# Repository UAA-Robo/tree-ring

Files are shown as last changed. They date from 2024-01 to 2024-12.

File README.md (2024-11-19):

# Tree Ring Imaging Machine (TRIM)

Documentation can be viewed at [uaa-robo.github.io/tree-ring](https://uaa-robo.github.io/tree-ring/) and in the docs folder.

This code controls the Amscope camera (our model is the MU500 and MU1000).

The following files are taken from the SDK provided by AmScope [here](https://amscope.com/pages/software-downloads) when you select your camera and model:
* amcam.py - this file provides an API for the camera. For more information about the API, see [API.pdf](API.pdf).
* simplest.py - this file provides a simple example that opens the camera and grabs frames from the camera, though it does not display these frames.
* qt.py - this file provides an example that grabs frames from the camera and renders them in a GUI.
* libamacam.dylib - needed for mac
* win/ - contains drivers and dlls needed for windows

We created the following files:
* camera.py - Interfaces with images from the amcam or the webcam if no amcam is present.
* gui.py - Displays a gui that the user can use to run the automation script. Displays camera feed.
* automationScript.py -  Script that rotates the motor to shift the platform and trigger the camera to take pctures.

## Setup & Running
For setup, run `python -m pip install -r requirements.txt` to install the python requirements needed.

To execute this program run `python gui.py` in this directory.

## Bundle program into an executable for Windows
To compile this program, double-click on the `build.bat` script. An executable will be generated
in the dist folder.

Note: When building the program in "windowed" mode or "noconsole", Windows thinks its a virus. Building
it with the console window attached when running prevents that from happening.

<!-- Old instructions -->
<!-- To compile this program go open the terminal in the directory of gui.py and run `python -m PyInstaller gui.py --onefile --windowed`. This will not work on Mac due to strict camera permission.

When building the program into a binary, Windows will throw a 'severe' threat warning. This is
because the software lacks an official Microsoft signature. To bypass this, open Windows Security,
click on 'Virus & threat protection,' and click on the link 'Manage settings' under 'Virus & threat
protection settings.' At the bottom of this menu there is a link to 'Add or remove exclusions.'
Add an exclusion of the type 'Folder,' and select the directory containing the program. Now running
the above command will successfully build the executable. -->

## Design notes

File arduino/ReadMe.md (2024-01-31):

To run the arduino code make sure to set the board type to arduino nano in the arduino IDE

Arguments that can be passed to Arduino
Z = Zero Platform
H = Make Motor Turn Clockwise
L = Make Motor Turn CounterClockwise
R = Move Motor 1 Increment
+ = Increase Motor Turn Length by 1/10
- = Decrease Motor Turn Length by 1/10
= = Get Motor Turn Length

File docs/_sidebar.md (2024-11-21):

* [Instructions](instructions.md)
* [How to Build](how_to_build/construction_instructions.md)
    * [Bill of Materials](how_to_build/BOM.md)
* [Upgrades](upgrades.md)
* [Troubleshooting](troubleshooting/troubleshooting.md)
    * [Motor Not Moving](troubleshooting/motor_movement.md)
    * [Motor is Loud](troubleshooting/motor_noises.md)
    * [No Arduino Connected](troubleshooting/no_arduino.md)
    * [No Camera Detected](troubleshooting/no_camera.md)
    * [Optimal Camera Settings](troubleshooting/optimal_settings.md)
* [Code Overview](code.md)
* [Contributing](contributing.md)

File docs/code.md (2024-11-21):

# Code Explanations
Refer to the comments in our code in our github for more in-depth explanations of each function. Below iss an overview.

## GUI 
* gui.py
The GUI class contains all the logic for displaying the user interface. It has a callback to Camera to display the camera video stream to the user. The GUI will display any warnings or errors that show up as popups.The user can enter the following information:
* **Image/Core name**: This is used to name the images when saving, with a prepended image number. For example if `core_alpha` is entered, the images would be named `core_alpha_1.jpg`, `core_alpha_2.jpg`, etc
* **Core Length (cm)**: This is the length of the core in cm.
* **Shift Length (mm)**: This is the length to shift the core sample after taking a picture.

Then the user can start the automation program in the Automation class. We suggest setting the image path to the desired location where you want TRIM to put the folder of images it creates, otherwise it will default to the desktop. After selection, the automation immediately starts. The user can stop the program at any time by pressing the pause button, and can later resume the automation by pressing play.

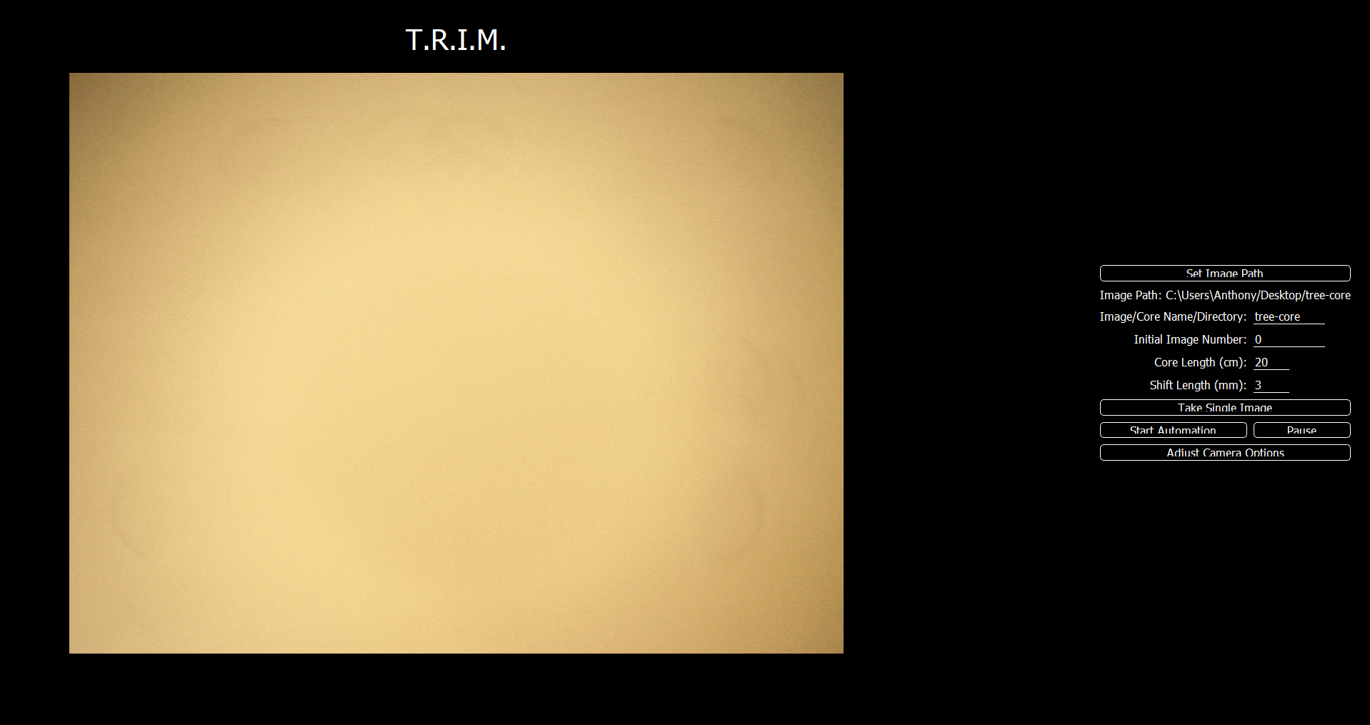
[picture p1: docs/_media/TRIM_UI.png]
GUI


### Camera Options

Pressing the **Adjust Camera Options** button will open a new window that allows the user to adjust camera video and save options. Pressing **Save** will save them to a file called `camera_configuration.yaml` in the directory where the program is located. By default, the program loads the settings from this file on startup. Pressing **Reset** will reset any changes back to this file, or if it is missing, the optimal settings. If you need the actual default settings in the API or a copy of the optimal settings file, go to [this link](troubleshooting/optimal_settings.md) to get the original file.

## Automation 
* automationScript.py

The Automation class contains all the code for automating the tree ring process. It references the Camera class (in camera.py) to save images and the Arduino class (in the same file) to send signals to the arduino to connect and rotate the motor. The primary method of this class is start_automation. It calculates the number of times to move the tree ring based on the length input. Then it moves the platform that many times by that length, taking and saving a picture before each shift. 

The Arduino Class is a wrapper for the commands sent to the Arduino. The Arduino defaults to a shift length of 3mm and the following commands are Currently the following high level methods are implemented:
* `connect_to_arduino` - Attempts to connect to the arduino.
* `update_shift_length` - Updates the shift length that the arduino spins the motor (defaults to 3mm).
* `shift_right` - Spins the motor left to shift the platform RIGHT by the shift length.

## Camera 
* camera.py
* amcam.py (Amcam API)
* amcam.dll, libamcam.dylib (compiled C code used by amcam.py)
* /win (windows drivers)

The Camera class holds all properties for the camera and wraps all interactions with it. When the program begins and initializes the Camera, a callback method is loaded into the Amcam API. The Amcam API controls the camera, and by manipulating the contents of this callback method, we can choose to act on the events being sent from the camera (in this case we use `AMCAM_EVENT_IMAGE` and `AMCAM_EVENT_STILLIMAGE). The microscope image quality is left as default in all settings but the saturation, which is adjusted to around 37.6% of its range (96 / 255).

### Using the Microscope Camera
The Amcam camera starts its own thread, seen by `StartPullModeWithCallback()` in `connect_stream`, and runs the callback method first loaded in the init method. From then on, the camera runs asynchronously to the main thread, calling the static method, `camera_callback`. This callback pulls the camera's image into a byte array, converts it to a QImage, and saves it in the class for extraction by the program later. When an image is taken, the camera pauses the preview to take a still image (a full-resolution picture). The callback waits for a signal from the camera that it is done before saving the image to the specified directory.

### No Microscope Camera
If the microscope camera could not be loaded in the first place, the **cv2** library is used to load the next available camera (called `WEBCAM` in the camera type). In this case the Amcam API is not running its own thread, so instead of using the callback method, `connect_stream` starts a new thread for streaming from this camera, paralleling the Amcam API's behavior.

## Arduino 
* arduino/tree-ring/tree-ring.ino

The tree-ring.ino file holds the entirety of the code on the arduino. When powered on the arduino first runs the `setup()` function and once that is complete it will immediately start the `loop()` function. From there the arduino waits for a signal from the computer to start doing any actions.

Arguments that can be passed to Arduino  
`H`  Make Motor Turn Clockwise  
`L`  Make Motor Turn CounterClockwise  
`R`  Move Motor 1 Increment  
`+`  Increase Motor Turn Length by 1/10  
`-`  Decrease Motor Turn Length by 1/10  
`=`  Get Motor Turn Length

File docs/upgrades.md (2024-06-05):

# Upgrade Instructions
This guide provides easy-to-follow instructions on upgrading components of the TRIM software
solution.

## Camera
TRIM was originally designed for AmScope cameras, and so it utilizes the AmScope SDK. This means that AmScope cameras are preferred. As a backup, TRIM also supports cameras covered by the OpenCV library, but the advanced features are not supported for these cameras and they will take images at their default resolutions. It recommended to stay within the AmScope family, __.

The SDK used is specific to the camera, however. This means that it is necessary to install a new SDK on a new camera upgrade. These are the steps to upgrade the camera:

1. The new camera comes with a USB flash drive containing drivers. It also contains an up-to-date SDK that supports the new camera.
    - Plug the flash drive in and open the folder. First install the drivers. This can be done by either executing the `AmScopeMicroDshowSetup.exe` in the SDK folder, or installing the drivers manually (located in SDK/amcamsdk.20231217.zip/win/drivers/). The former method also installs the official AmScope software.
2. After installing the drivers, open a new window to the tree-ring source code folder.
3. Remove (keep somewhere else in case) the following files: `amcam.py`, `amcam.dll`, and `libamcam.dylib`.
4. Open up SDK/amcamsdk.20231217.zip and unzip it. Inside this directory, copy the following files into the root folder of the tree-ring source code folder:
    - `python/amcam.py`
    - `win/x64/amcam.dll`
    - `mac/x64+arm64/libamcam.dylib`

That should be it! The camera should be detected by the software now.

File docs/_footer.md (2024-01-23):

<b><br>
____
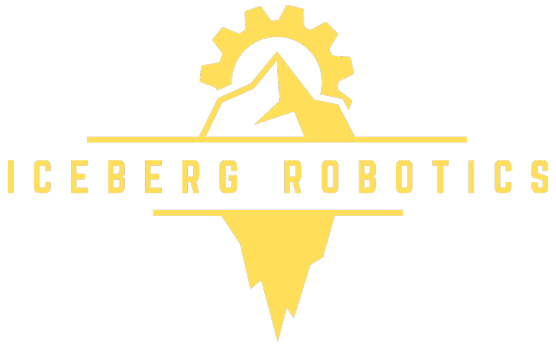
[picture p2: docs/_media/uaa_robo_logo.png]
:size=8%
 
<!-- ***Documentation maintained by [UAA Iceberg Robotics](http://uaarobotics.com).*** -->

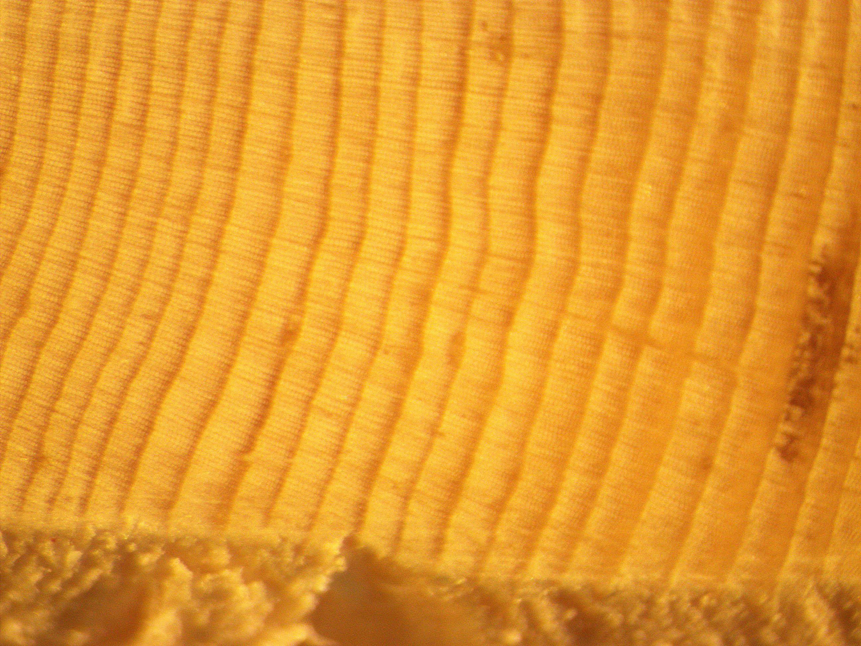
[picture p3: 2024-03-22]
Tree_Core_000.jpg

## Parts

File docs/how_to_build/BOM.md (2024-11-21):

# Bill of Materials

If this is not filled out by 11/22/2024 please create an issue on the Github repository.

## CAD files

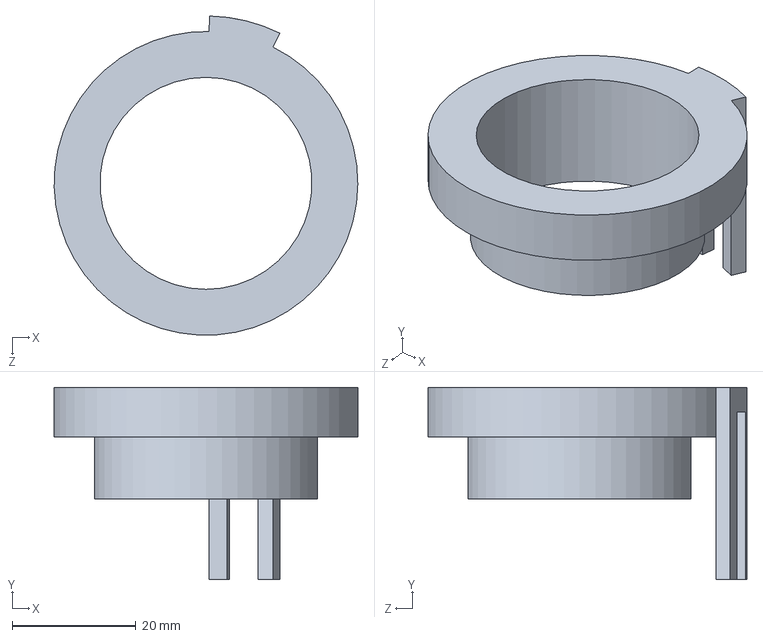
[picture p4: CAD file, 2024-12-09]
cad_models/TRIM MU500 Adapter.SLDPRT
49.0 x 31.0 x 51.5 mm

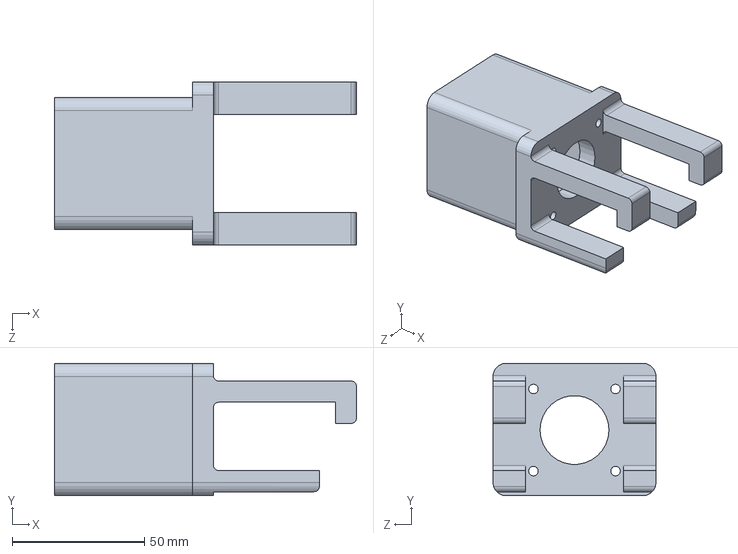
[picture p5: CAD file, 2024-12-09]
cad_models/TRIM Motor Mount.SLDPRT
114.0 x 50.0 x 61.5 mm

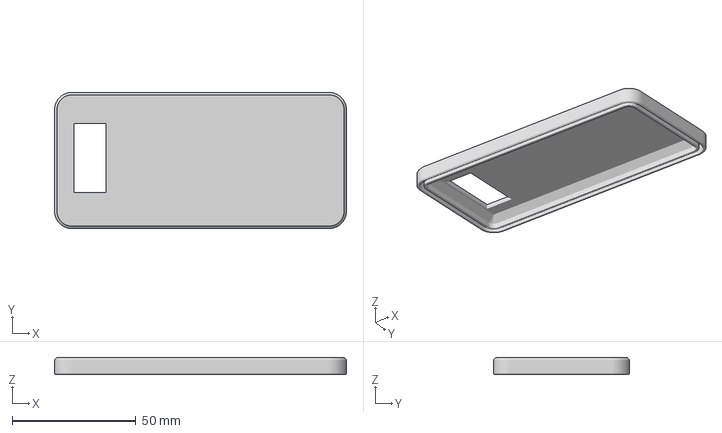
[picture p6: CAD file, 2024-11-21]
cad_models/TRIM Lid.3mf
118.2 x 55.1 x 7.00 mm

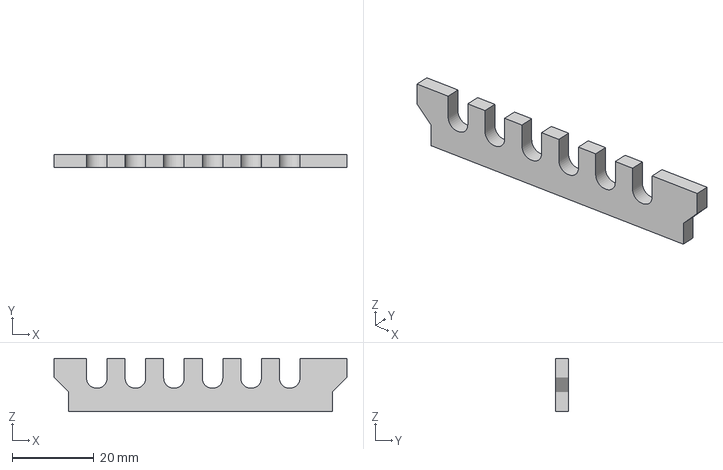
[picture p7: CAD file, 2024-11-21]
cad_models/TRIM Board Lock.3mf
71.5 x 3.20 x 13.0 mm

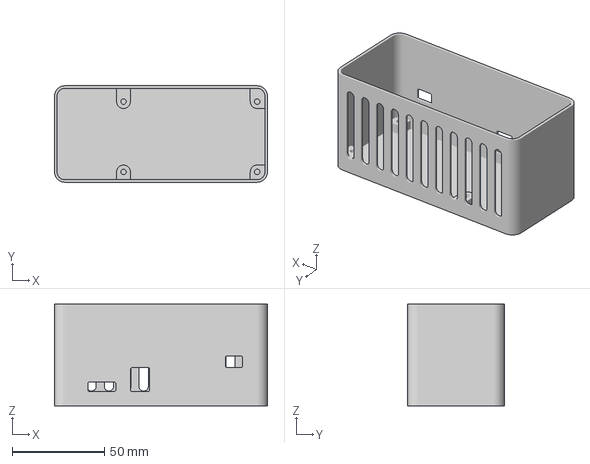
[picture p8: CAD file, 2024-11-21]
cad_models/TRIM Enclosure.3mf
115.4 x 52.3 x 55.0 mm

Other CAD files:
cad_models/TRIM MU500 Adapter.STL
cad_models/TRIM Motor Mount.STL

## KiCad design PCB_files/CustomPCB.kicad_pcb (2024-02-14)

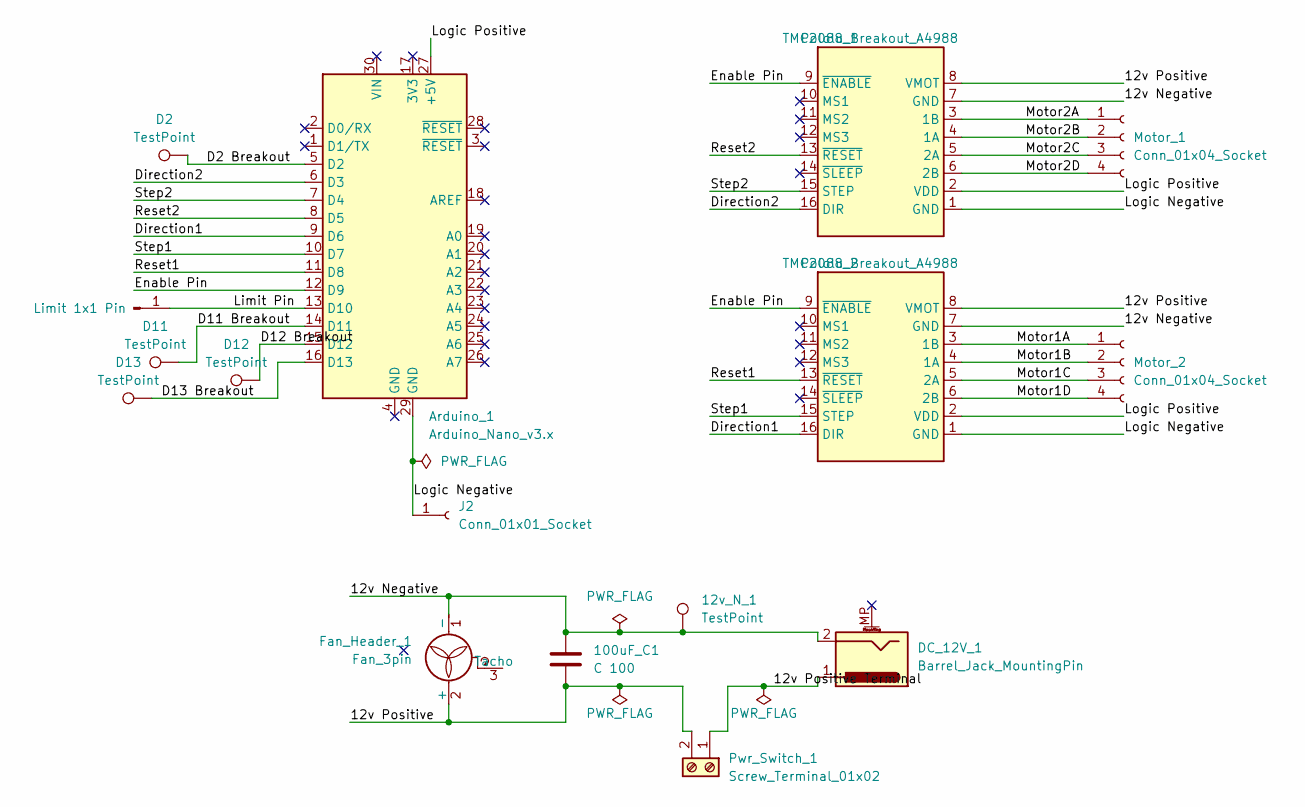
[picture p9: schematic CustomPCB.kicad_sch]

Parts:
12v_N_1: TestPoint; TestPoint_Pad_1.5x1.5mm
100uF_C1: C 100; CP_Radial_D8.0mm_P5.00mm
Arduino_1: Arduino_Nano_v3.x; Arduino_Nano
D2, D11, D12, D13: TestPoint; TestPoint_Pad_1.5x1.5mm
DC_12V_1: Barrel_Jack_MountingPin; BarrelJack_Horizontal
Fan_Header_1: Fan_3pin; FanPinHeader_1x03_P2.54mm_Vertical
J1: Limit 1x1 Pin; PinHeader_1x01_P2.54mm_Vertical
J2: Conn_01x01_Socket; PinHeader_1x01_P2.54mm_Vertical
Motor_1, Motor_2: Conn_01x04_Socket; PinSocket_1x04_P2.54mm_Vertical
Pwr_Switch_1: Screw_Terminal_01x02; TerminalBlock_bornier-2_P5.08mm
TMC2088_1, TMC2088_2: Pololu_Breakout_A4988; Pololu_Breakout-16_15.2x20.3mm

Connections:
/12v Negative: 12v_N_1.1, 100uF_C1.2, DC_12V_1.2, Fan_Header_1.1 (-), TMC2088_1.7 (GND), TMC2088_2.7 (GND)
/12v Positive: 100uF_C1.1, Fan_Header_1.2 (+), Pwr_Switch_1.2, TMC2088_1.8 (VMOT), TMC2088_2.8 (VMOT)
/12v Positive Terminal: DC_12V_1.1, Pwr_Switch_1.1
/D2 Breakout: Arduino_1.5 (D2), D2.1
/D11 Breakout: Arduino_1.14 (D11), D11.1
/D12 Breakout: Arduino_1.15 (D12), D12.1
/D13 Breakout: Arduino_1.16 (D13), D13.1
/Direction1: Arduino_1.9 (D6), TMC2088_2.16 (DIR)
/Direction2: Arduino_1.6 (D3), TMC2088_1.16 (DIR)
/Enable Pin: Arduino_1.12 (D9), TMC2088_1.9 (~ENABLE), TMC2088_2.9 (~ENABLE)
/Limit Pin: Arduino_1.13 (D10), J1.1
/Logic Negative: Arduino_1.29 (GND), J2.1, TMC2088_1.1 (GND), TMC2088_2.1 (GND)
/Logic Positive: Arduino_1.27 (+5V), TMC2088_1.2 (VDD), TMC2088_2.2 (VDD)
/Motor1A: Motor_2.1, TMC2088_2.3 (1B)
/Motor1B: Motor_2.2, TMC2088_2.4 (1A)
/Motor1C: Motor_2.3, TMC2088_2.5 (2A)
/Motor1D: Motor_2.4, TMC2088_2.6 (2B)
/Motor2A: Motor_1.1, TMC2088_1.3 (1B)
/Motor2B: Motor_1.2, TMC2088_1.4 (1A)
/Motor2C: Motor_1.3, TMC2088_1.5 (2A)
/Motor2D: Motor_1.4, TMC2088_1.6 (2B)
/Reset1: Arduino_1.11 (D8), TMC2088_2.13 (~RESET)
/Reset2: Arduino_1.8 (D5), TMC2088_1.13 (~RESET)
/Step1: Arduino_1.10 (D7), TMC2088_2.15 (STEP)
/Step2: Arduino_1.7 (D4), TMC2088_1.15 (STEP)

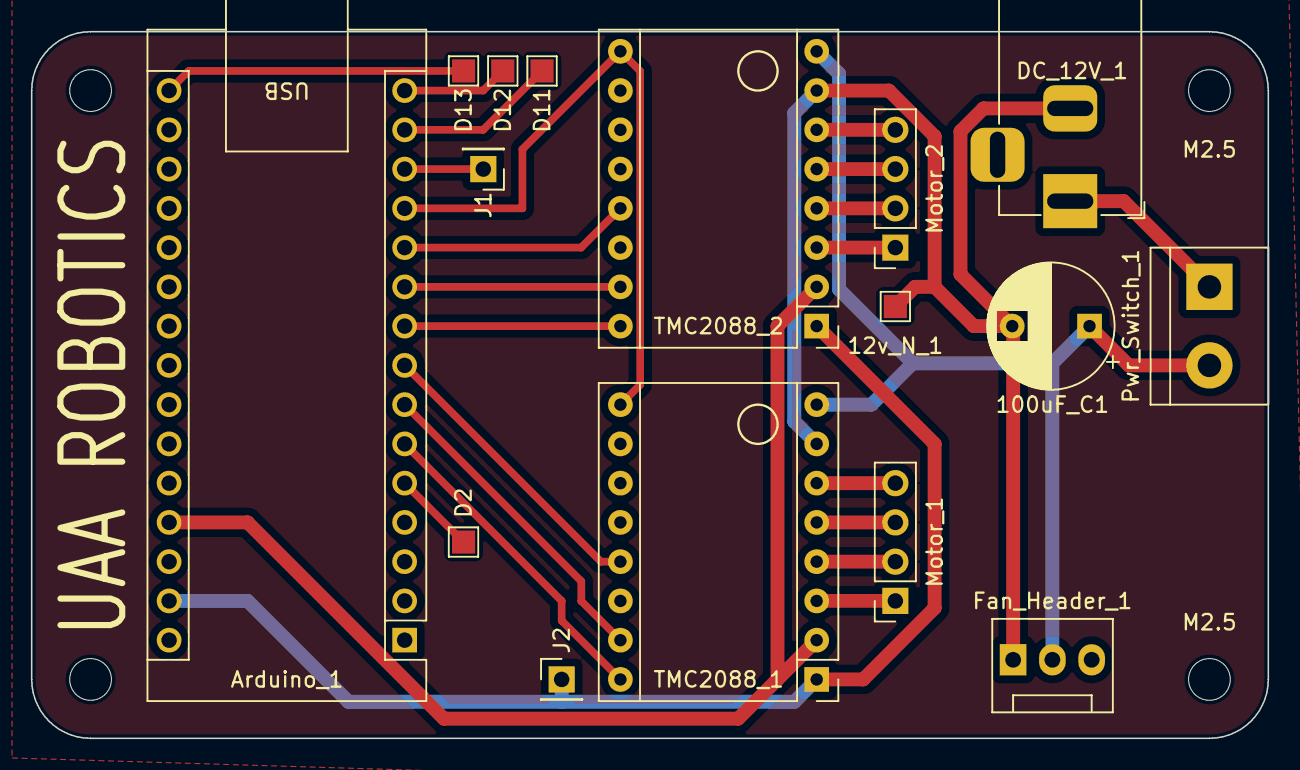
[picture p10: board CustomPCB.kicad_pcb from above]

Board: 2 copper layers, 80.0 x 45.7 mm, 20 parts (0 on the bottom side), 25 nets.

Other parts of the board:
M2.5, M2.5#2, M2.5#3, M2.5#4: MountingHole_2.7mm_M2.5

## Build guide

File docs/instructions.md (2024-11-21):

# Instructions for Use

1. Open the Application.

     

2. Setup your tree ring sample on the tray, so it is at the left edge of the microscope camera. Make sure too focus the camera properly.

3. Set the path where you would like TRIM to put the images.

4. Input your sample length (default is 20cm), and the amount you would like shift the sample each time (default is 3mm).

5. Select "Start Automation".

6. Let the script run. When it finishes it will say "Automation Stopped".

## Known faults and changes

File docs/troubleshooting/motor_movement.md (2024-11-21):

# Motor is not Moving

If the motor is not moving, please ensure that the switch ontop of TRIM's box is flipped to the ON position and that it is plugged in. If it is still not moving, please unseat and reseat all motor wires and ensure the motor drivers are pressed firmly in place.

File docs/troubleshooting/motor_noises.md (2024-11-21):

# Motor is Making Loud Noises

If the motor is loud please try changing the order of the motor's wires. This is often caused by the wires being in the wrong order.

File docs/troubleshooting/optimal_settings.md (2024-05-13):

# Optimal Settings for the Camera

The camera has a number of defaults for its image settings. However, through testing these have been found to be sub-optimal. The following table demonstrates the default and optimal settings for each camera setting.

| Camera Setting         | Range     | Default  | Optimal   |
| ---------------------- | --------- | -------- | --------- |
| Auto-Expo Enabled      | 1/0       |  1       |  0        |
| Auto Exposure Target   |   16~235  |  120     |  120      |
| Temperature            | 2000~15000|  6503    |  11616    |
| Tint                   | 200~2500  |  1000    |  925      |
| Level Range            | 0~255 x 4 | L(0,0,0,0) H(255,255,255,255)    | L(0,0,0,0) H(255,255,255,255)   |
| Contrast               | -100~100  |  0       |  0        |
| Hue                    | -180~180  |  0       |  0        |
| Saturation             | 0~255     |  128     |  126      |
| Brightness             | -64~64    |  0       |  -64      |
| Gamma                  | 20~180    |  100     |  100      |
| WBGain                 | -127~127 x 3   |  (0,0,0)       |  (0,0,0)       |
| Sharpening             | 0~500     |  0       |  500      |
| Linear Tone Mapping    | 1/0       |  1       |  0        |
| Curved Tone Mapping    | 2/1/0     |  2 (Logarithmic)     |  1 (Polynomial)      |

To configure the camera to the optimal settings, copy the following text block into a file called
`camera_configuration.yaml` in the directory where the program's exe is in.

**For a Leica KL 1500LCD light:**
```yaml
auto_expo: 0
brightness: 16
contrast: 0
curve: Polynomial
exposure: 50
fformat: tiff
gamma: 100
hue: 0
levelrange_high:
- 255
- 255
- 255
- 255
levelrange_low:
- 0
- 0
- 0
- 0
linear: 0
saturation: 96
sharpening: 500
temp: 6503
tint: 1000
wbgain:
- 0
- 0
- 0

```

**For a ring light:**
```yaml
auto_expo: 0
brightness: -64
contrast: 0
curve: Polynomial
exposure: 120
fformat: tiff
gamma: 100
hue: 0
levelrange_high:
- 255
- 255
- 255
- 255
levelrange_low:
- 0
- 0
- 0
- 0
linear: 0
saturation: 126
sharpening: 500
temp: 11616
tint: 925
wbgain:
- 0
- 0
- 0

```

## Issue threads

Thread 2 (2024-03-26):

### ISSUE TITLE
Capturing exposure events

### ISSUE THREAD

**Issue by richbai90** [UAA-Robo/tree-ring#2]
Hello,

I am writing because you are the only repo on Github I could find that was actively maintaining a project that utilizes the Amscope API. I'm using the AMCAM_EVENT_EXPO_START and AMCAM_EVENT_EXPO_END events, respectively, but they are not triggered when using pull mode, at least not when the camera is in video mode. Have you tried to use these events or other events besides AMCAM_EVENT_IMAGE in your work?

**Comment by Dawson-Packer** [comment]
Our project has only used AMCAM_EVENT_IMAGE so far so I’m sorry to say we can’t help you. If we learn anything new, we’ll make sure to send it your way.

**Comment by richbai90** [comment]
It's not supported with our camera. Closing, but thank you for replying.

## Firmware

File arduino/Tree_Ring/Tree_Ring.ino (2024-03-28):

int DIRECTION_PIN = 3;
int STEPPER_PIN = 4;
int LIMIT_SWITCH_PIN = 10;
int ENABLE_PIN = 9;
int RESET_PIN = 5;

int incoming_byte;

bool IS_CLOCKWISE = true;
bool IS_ACTIVE = false;

int active_counter = 0;
int rotate_amount = 161;//1600; //steps per revolution for 200 pulses = 360 degree full cycle rotation
int millimeters = 30;
int original_millimeters = millimeters;
int actual_movement = rotate_amount * millimeters;

void setup()
{
  /* 
	@brief   Setup the arduino upon power on.
  */
  pinMode(ENABLE_PIN, OUTPUT);
  pinMode(DIRECTION_PIN, OUTPUT);
  pinMode(STEPPER_PIN, OUTPUT);
  pinMode(LIMIT_SWITCH_PIN, INPUT_PULLUP);
  digitalWrite(DIRECTION_PIN, LOW);
  digitalWrite(STEPPER_PIN, LOW);
  activate();
  Serial.begin(9600);
}


void step(boolean dir,int steps)
 {
  /*
	@brief   This makes the motor move by a set amount. 
  @param dir   Direction the Motor Moves.
  @param stepts   Steps for the motor to turn. Minimum number of steps is 600, add more to go slower.
  */

 digitalWrite(DIRECTION_PIN,dir);

 for(int i=0;i<steps;i++)
 {
   digitalWrite(STEPPER_PIN, HIGH);
   delayMicroseconds(150);//Adjust the speed of motor. Increase the value, motor speed become slower.
   digitalWrite(STEPPER_PIN, LOW);
   delayMicroseconds(150);
 }
}

void activate(){
  /* 
	@brief   Wake up the motor driver.
  */
  if(!IS_ACTIVE){
    active_counter = 0;
    digitalWrite(ENABLE_PIN, LOW);
    digitalWrite(RESET_PIN, LOW);
    IS_ACTIVE = true;
    delayMicroseconds(1000);
  }
}


void deactivate(){
  /* 
	@brief   Put the motor driver to sleep. This saves power and makes the motor not heat up.
  */
  digitalWrite(ENABLE_PIN, HIGH);
  digitalWrite(RESET_PIN, HIGH);
  IS_ACTIVE = false;
}


void loop()
{
  /* 
	@brief   Update loop.
  */
  if(Serial.available()) {
    incoming_byte = Serial.read();
    if(incoming_byte == 72) { // H Set platform to rotate clockwise.
      Serial.write("Clockwise");
      IS_CLOCKWISE = true;
    } 
    if(incoming_byte == 76) { // L Set platform to rotate anticlockwise.
      Serial.write("AntiClockwise");
      IS_CLOCKWISE = false;
    }
    if(incoming_byte == 77) { // M Move the platform.
      activate();
      step(IS_CLOCKWISE, actual_movement);
    }
    if(incoming_byte == 82) { // R Reset Rotation Amount.
      millimeters = original_millimeters;
      Serial.write(millimeters);
    }
    if(incoming_byte == 43) { // + Increase Rotation Amount.
      millimeters = millimeters + 1;
      Serial.write(millimeters);
    }
    if(incoming_byte == 45) { // - Decrease Rotation amount.
      millimeters = millimeters - 1;
      Serial.write(millimeters);
    }
    if(incoming_byte == 61) { // = Get current Rotation Amount.
      Serial.write(millimeters);
    }
    actual_movement = rotate_amount * millimeters;
  }

  // Put motor to sleep if not in use.
  active_counter++;
  if(active_counter == 6000) {
    deactivate();
  }
}

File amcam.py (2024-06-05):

"""Version: 55.24172.20231217
We use ctypes to call into the amcam.dll/libamcam.so/libamcam.dylib API,
the python class Amcam is a thin wrapper class to the native api of amcam.dll/libamcam.so/libamcam.dylib.
So the manual en.html(English) and hans.html(Simplified Chinese) are also applicable for programming with amcam.py.
See them in the 'doc' directory:
   (1) en.html, English
   (2) hans.html, Simplified Chinese
"""
import sys, ctypes, os.path

AMCAM_MAX = 128

AMCAM_FLAG_CMOS                = 0x00000001          # cmos sensor
AMCAM_FLAG_CCD_PROGRESSIVE     = 0x00000002          # progressive ccd sensor
AMCAM_FLAG_CCD_INTERLACED      = 0x00000004          # interlaced ccd sensor
AMCAM_FLAG_ROI_HARDWARE        = 0x00000008          # support hardware ROI
AMCAM_FLAG_MONO                = 0x00000010          # monochromatic
AMCAM_FLAG_BINSKIP_SUPPORTED   = 0x00000020          # support bin/skip mode
AMCAM_FLAG_USB30               = 0x00000040          # usb3.0
AMCAM_FLAG_TEC                 = 0x00000080          # Thermoelectric Cooler
AMCAM_FLAG_USB30_OVER_USB20    = 0x00000100          # usb3.0 camera connected to usb2.0 port
AMCAM_FLAG_ST4                 = 0x00000200          # ST4
AMCAM_FLAG_GETTEMPERATURE      = 0x00000400          # support to get the temperature of the sensor
AMCAM_FLAG_HIGH_FULLWELL       = 0x00000800          # high fullwell capacity
AMCAM_FLAG_RAW10               = 0x00001000          # pixel format, RAW 10bits
AMCAM_FLAG_RAW12               = 0x00002000          # pixel format, RAW 12bits
AMCAM_FLAG_RAW14               = 0x00004000          # pixel format, RAW 14bits
AMCAM_FLAG_RAW16               = 0x00008000          # pixel format, RAW 16bits
AMCAM_FLAG_FAN                 = 0x00010000          # cooling fan
AMCAM_FLAG_TEC_ONOFF           = 0x00020000          # Thermoelectric Cooler can be turn on or off, support to set the target temperature of TEC
AMCAM_FLAG_ISP                 = 0x00040000          # ISP (Image Signal Processing) chip
AMCAM_FLAG_TRIGGER_SOFTWARE    = 0x00080000          # support software trigger
AMCAM_FLAG_TRIGGER_EXTERNAL    = 0x00100000          # support external trigger
AMCAM_FLAG_TRIGGER_SINGLE      = 0x00200000          # only support trigger single: one trigger, one image
AMCAM_FLAG_BLACKLEVEL          = 0x00400000          # support set and get the black level
AMCAM_FLAG_AUTO_FOCUS          = 0x00800000          # support auto focus
AMCAM_FLAG_BUFFER              = 0x01000000          # frame buffer
AMCAM_FLAG_DDR                 = 0x02000000          # use very large capacity DDR (Double Data Rate SDRAM) for frame buffer. The capacity is not less than one full frame
AMCAM_FLAG_CG                  = 0x04000000          # support Conversion Gain mode: HCG, LCG
AMCAM_FLAG_YUV411              = 0x08000000          # pixel format, yuv411
AMCAM_FLAG_VUYY                = 0x10000000          # pixel format, yuv422, VUYY
AMCAM_FLAG_YUV444              = 0x20000000          # pixel format, yuv444
AMCAM_FLAG_RGB888              = 0x40000000          # pixel format, RGB888
AMCAM_FLAG_RAW8                = 0x80000000          # pixel format, RAW 8 bits
AMCAM_FLAG_GMCY8               = 0x0000000100000000  # pixel format, GMCY, 8 bits
AMCAM_FLAG_GMCY12              = 0x0000000200000000  # pixel format, GMCY, 12 bits
AMCAM_FLAG_UYVY                = 0x0000000400000000  # pixel format, yuv422, UYVY
AMCAM_FLAG_CGHDR               = 0x0000000800000000  # Conversion Gain: HCG, LCG, HDR
AMCAM_FLAG_GLOBALSHUTTER       = 0x0000001000000000  # global shutter
AMCAM_FLAG_FOCUSMOTOR          = 0x0000002000000000  # support focus motor
AMCAM_FLAG_PRECISE_FRAMERATE   = 0x0000004000000000  # support precise framerate & bandwidth, see AMCAM_OPTION_PRECISE_FRAMERATE & AMCAM_OPTION_BANDWIDTH
AMCAM_FLAG_HEAT                = 0x0000008000000000  # support heat to prevent fogging up
AMCAM_FLAG_LOW_NOISE           = 0x0000010000000000  # support low noise mode (Higher signal noise ratio, lower frame rate)
AMCAM_FLAG_LEVELRANGE_HARDWARE = 0x0000020000000000  # hardware level range, put(get)_LevelRangeV2
AMCAM_FLAG_EVENT_HARDWARE      = 0x0000040000000000  # hardware event, such as exposure start & stop
AMCAM_FLAG_LIGHTSOURCE         = 0x0000080000000000  # embedded light source
AMCAM_FLAG_FILTERWHEEL         = 0x0000100000000000  # astro filter wheel
AMCAM_FLAG_GIGE                = 0x0000200000000000  # 1 Gigabit GigE
AMCAM_FLAG_10GIGE              = 0x0000400000000000  # 10 Gigabit GigE
AMCAM_FLAG_5GIGE               = 0x0000800000000000  # 5 Gigabit GigE
AMCAM_FLAG_25GIGE              = 0x0001000000000000  # 2.5 Gigabit GigE
AMCAM_FLAG_AUTOFOCUSER         = 0x0002000000000000  # astro auto focuser
AMCAM_FLAG_LIGHT_SOURCE        = 0x0004000000000000  # stand alone light source
AMCAM_FLAG_CAMERALINK          = 0x0008000000000000  # camera link
AMCAM_FLAG_CXP                 = 0x0010000000000000  # CXP: CoaXPress
AMCAM_FLAG_RAW12PACK           = 0x0020000000000000  # pixel format, RAW 12bits packed
AMCAM_FLAG_SELFTRIGGER         = 0x0040000000000000  # self trigger
AMCAM_FLAG_RAW11               = 0x0080000000000000  # pixel format, RAW 11bits
AMCAM_FLAG_GHOPTO              = 0x0100000000000000  # ghopto sensor

AMCAM_EVENT_EXPOSURE           = 0x0001          # exposure time or gain changed
AMCAM_EVENT_TEMPTINT           = 0x0002          # white balance changed, Temp/Tint mode
AMCAM_EVENT_CHROME             = 0x0003          # reversed, do not use it
AMCAM_EVENT_IMAGE              = 0x0004          # live image arrived, use PullImageXXXX to get this image
AMCAM_EVENT_STILLIMAGE         = 0x0005          # snap (still) frame arrived, use PullStillImageXXXX to get this frame
AMCAM_EVENT_WBGAIN             = 0x0006          # white balance changed, RGB Gain mode
AMCAM_EVENT_TRIGGERFAIL        = 0x0007          # trigger failed
AMCAM_EVENT_BLACK              = 0x0008          # black balance changed
AMCAM_EVENT_FFC                = 0x0009          # flat field correction status changed
AMCAM_EVENT_DFC                = 0x000a          # dark field correction status changed
AMCAM_EVENT_ROI                = 0x000b          # roi changed
AMCAM_EVENT_LEVELRANGE         = 0x000c          # level range changed
AMCAM_EVENT_AUTOEXPO_CONV      = 0x000d          # auto exposure convergence
AMCAM_EVENT_AUTOEXPO_CONVFAIL  = 0x000e          # auto exposure once mode convergence failed
AMCAM_EVENT_ERROR              = 0x0080          # generic error
AMCAM_EVENT_DISCONNECTED       = 0x0081          # camera disconnected
AMCAM_EVENT_NOFRAMETIMEOUT     = 0x0082          # no frame timeout error
AMCAM_EVENT_AFFEEDBACK         = 0x0083          # auto focus information feedback
AMCAM_EVENT_FOCUSPOS           = 0x0084          # focus positon
AMCAM_EVENT_NOPACKETTIMEOUT    = 0x0085          # no packet timeout
AMCAM_EVENT_EXPO_START         = 0x4000          # hardware event: exposure start
AMCAM_EVENT_EXPO_STOP          = 0x4001          # hardware event: exposure stop
AMCAM_EVENT_TRIGGER_ALLOW      = 0x4002          # hardware event: next trigger allow
AMCAM_EVENT_HEARTBEAT          = 0x4003          # hardware event: heartbeat, can be used to monitor whether the camera is alive
AMCAM_EVENT_TRIGGER_IN         = 0x4004          # hardware event: trigger in
AMCAM_EVENT_FACTORY            = 0x8001          # restore factory settings
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

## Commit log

2024-01-05 added arduino code
2024-01-07 Started camera implementation, testing with webcam for the time being
2024-01-07 Started microscope camera implementation, needs testing at lab
2024-01-10 Testing camera
2024-01-10 Added close method to Camera (unused)
2024-01-11 Automation framework
2024-01-12 Camera streaming revised
2024-01-12 Updated camera docstrings
2024-01-14 Wrapped Arduino code in class
2024-01-14 Created automation class as it's own thread
2024-01-14 Threading now works with decorator
2024-01-16 Passing args to thread works
2024-01-16 Fixed threading and added logic for inputing core length
2024-01-16 Added shift logic and arduino check
2024-01-16 Added camera callback
2024-01-23 Added camera window grow/shrink function
2024-01-24 Updated Arduino readme
2024-01-24 Added first CAD model
    [mu500_adapter_1.stl]
2024-01-30 Added Camera class documentation
2024-01-31 Added camera image quality adjustment methods
2024-02-06 Added PCB Files
    [CustomPCB-B_Cu.gbr, CustomPCB-B_Mask.gbr, CustomPCB-B_Paste.gbr, CustomPCB-B_Silkscreen.gbr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]
2024-02-06 updated PCB for JLCPCB's tolerances
    [CustomPCB-B_Cu.gbr, CustomPCB-B_Mask.gbr, CustomPCB-B_Paste.gbr, CustomPCB-B_Silkscreen.gbr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]
2024-02-07 Updated Arduino Documentation
2024-02-07 Added electronics box stl
    [electronics_box.stl]
2024-02-13 PCB V2
    [CustomPCB-B_Cu.gbr, CustomPCB-B_Mask.gbr, CustomPCB-B_Paste.gbr, CustomPCB-B_Silkscreen.gbr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]
2024-02-19 Added function prototypes and comments
2024-03-21 Messed with default camera options
2024-03-22 made motor not power on
2024-04-03 Updated defaults for camera settings based on last meeting
2024-04-05 Removed prints
2024-04-24 Started putting new camera settings in sliders
2024-04-30 Changed default camera settings to optimal
2024-05-02 Added hover button visual changes to camera options
2024-05-12 Added auto-exposure enable option to Camera Options, and allowed camera image settings to be modified even if the microscope isn't used
2024-05-13 Changed slider defaults to match optimal settings in camera.py
2024-06-05 Made still image resolution dependent on the camera instead of hardcoded
2024-06-05 Added instructions for upgrading the camera and updated build.bat
2024-11-21 Added 3D models for the enclosure
    [TRIM Board Lock.3mf, TRIM Enclosure.3mf, TRIM Lid.3mf, electronics_box.stl]
2024-12-09 Added new CADs
    [TRIM MU500 Adapter.SLDPRT, TRIM MU500 Adapter.STL, TRIM Motor Mount.SLDPRT, TRIM Motor Mount.STL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]
